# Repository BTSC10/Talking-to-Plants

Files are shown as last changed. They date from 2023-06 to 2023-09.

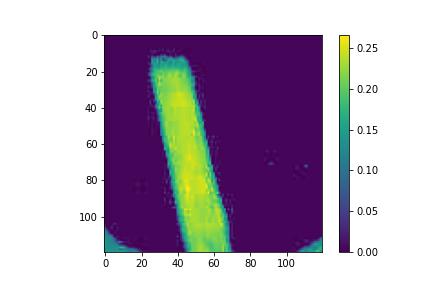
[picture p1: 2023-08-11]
Code/Offline Processing/Cultivar_assessment_SMFI/SMFI_stack__node_2_period_10_20230811_1433/false_coloured_stack/false_colour_91.jpg

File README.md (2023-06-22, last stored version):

# Talking-to-Plants
“Talking to Plants” via Active Digital Image Processing: Industry 4.0, IoT, Technology for Future Farming

This project is built upon the work complete by the below team members, where the project was continued as a Summer Internship

## Team Members:
| name  | user |
| ------------- | ------------- |
| Justin Tan | JSTUN9 |
| David Mohammadi | davidmo13|
| Momin Anwar | mominanwar|
| Mujhtaba Afzal | Gunflower123 |
| Sam Ryder | SamRyder |
| Flavia Dumitrica | flaviamihaela |
| Marton Gonczy | martongonczy |
| Artur Cruz | ArturCr |

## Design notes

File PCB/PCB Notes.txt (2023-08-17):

U14 - GND, SMFI LEDs not working ( + one set wrong way round, and one not working),

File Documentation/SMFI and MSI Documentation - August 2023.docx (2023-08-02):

SMFI AND MSI DOCUMENTATION

August 2023

Contents

# 1 Introduction

This document serves as the main documentation for the system develop during the 2022-23 academic year as the “Talking to plants” team project and the continuation of this work over the summer of 2023 – by Samuel Ryder and David Mohammadi. The system has been split up by subsystem – e.g., image capture, and gateway –, where both hardware and software are documented.

Currently two modes of operation exist for the device – MSI and SMFI. In SMFI mode one group of LEDs is sinusoidally modulated and a set number of images captured during one period. During MSI a single image is taken for each set of LEDs – 16 channels currently implemented.

# 2 Image Capture

## 2.1 Camera board

For this system the OpenMV H7 [1] is utilised, a global shutter module is also installed on this [2]. Further modifications are made to the camera: the included filter has been removed and replaced with an external filter [3].

## 2.2 LED board

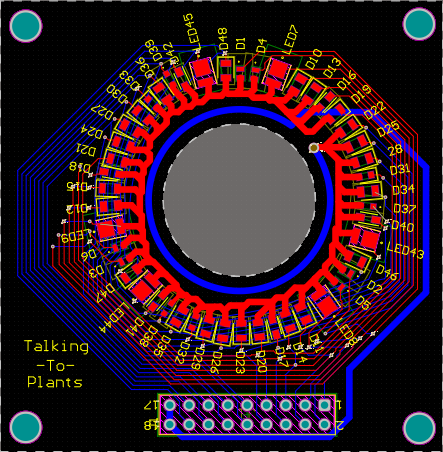
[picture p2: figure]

Figure 1, LED Board

Figure 2, LED Channel connections

Figure 1 shows the current configuration of the LED board, here 16 channels of 3 LEDs (48 in total) are connected. The LEDs within each channel are connected as shown in Figure 2. The wavelengths and chosen LEDs for each channel are listed in Table 1 below,

Table 1, LED Channels

Channel No. | Wavelength | LED
0
1
2 (SMFI)
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
The LED board PCB and schematic are given in [4].

## 2.3 LED Driver

The LED Driver serves to take the signals output from the camera and drive the LEDs, as well as this it serves as a connection between the camera and base box. The PCBs for this are given in [5].

The operation of driving the LEDs is explained below,

- The camera selects the appropriate output from the 1-to-16 multiplexer, where each output corresponds to one channel
- The camera output is set to a predetermined level
- A current driver is powered by this
- Current is sank through this via a header connecting to the LEDs

All channels – bar Channel 2 – show the same configuration, an LED driver connected to an output of the 1-to-16 multiplexer and the LED board header. Channel 2 is configured differently as this channel has the option of either being used in MSI or SMFI mode. Here after the 1-to-16 multiplexer output another multiplexer is found, this is a 1-to-2 multiplexer that allows either for an LED driver to be used (MSI), or a transistor (SMFI).

## 2.4 Camera Code

Two versions of camera code are provided in [6], SMFI and SMFI_MSI. Both operate in the same functionality, however, SMFI is used with the old hardware and SMFI_MSI with the new. Also, as can be seen from the names one is just SMFI and the other both modes. For sake of compactness only SMFI_MSI will be detailed here.

The basic operation of the code can be thought of as below,

- Setup is performed
- When an image capture is triggered, whether by button or timer, execute the main loop of code
- Set the multiplexers selects to match the desired operation
- Output the LED values
- Capture images
- Transmit images
- Perform more captures if required, or, update run parameters from cloud

The individual sections of code are described more thoroughly below.

# 3 References

[1] - https://openmv.io/products/openmv-cam-h7

[2] - https://openmv.io/products/global-shutter-camera-module

[3] - https://www.chroma.com/products/parts/at690-50m

[4] - https://github.com/SamRyder/Talking-to-Plants-Summer-Work/tree/main/PCB/LED%20Board

[5] - https://github.com/SamRyder/Talking-to-Plants-Summer-Work/tree/main/PCB/LED%20Driver

[6] - https://github.com/SamRyder/Talking-to-Plants-Summer-Work/tree/main/Code/Open%20MV%20Camera/Production_CODE

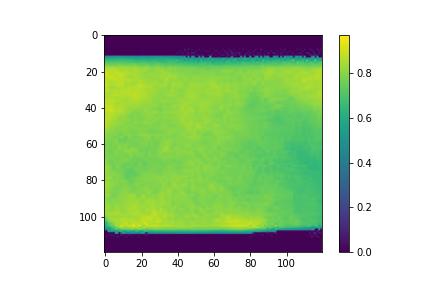
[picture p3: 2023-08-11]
Code/Offline Processing/Cultivar_assessment_SMFI/SMFI_stack__node_2_period_10_20230811_1407/false_coloured_stack/false_colour_89.jpg

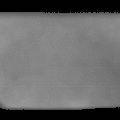
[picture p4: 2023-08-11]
Code/Offline Processing/Cultivar_assessment_SMFI/SMFI_stack__node_2_period_10_20230811_1407/Leaf-10s_fluorescence-frameno28.jpg

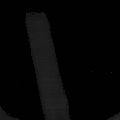
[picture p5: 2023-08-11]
Code/Offline Processing/Cultivar_assessment_SMFI/SMFI_stack__node_2_period_10_20230811_1433/Leaf-10s_fluorescence-frameno17.jpg

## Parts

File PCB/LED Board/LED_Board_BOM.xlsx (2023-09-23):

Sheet: LED_64_V1.3_BOM
Channel | Waveband | Part # | Qty/PCB | Qty | Mouser # | Mouser Link
0 | 395nm | ATS2012UV395 | 4 | 20 | 604-ATS2012UV395 | https://www.mouser.co.uk/ProductDetail/Kingbright/ATS2012UV395?qs=%252BEew9%252B0nqrCgwxEBSEvg7Q%3D%3D
1 | 415nm | ATS2012UV415 | 4 | 20 | 604-ATS2012UV415 | https://www.mouser.co.uk/ProductDetail/Kingbright/ATS2012UV415?qs=%252BEew9%252B0nqrDGuxxVD3buAQ%3D%3D
2 | 450nm | 150283DS73103 | 4 | 20 | 710-150283DS73103 | https://www.mouser.co.uk/ProductDetail/Wurth-Elektronik/150283DS73103?qs=GedFDFLaBXFC8uVfOF%252Bhgw%3D%3D
3 | 470nm | 599-0191-007F | 4 | 20 | 645-599-0191-007F | https://www.mouser.co.uk/ProductDetail/Dialight/599-0191-007F?qs=gTYE2QTfZfTbWzs5Ohdbbg%3D%3D
4 | 528nm | IN-S85ATG | 4 | 20 | 743-IN-S85ATG | https://www.mouser.co.uk/ProductDetail/Inolux/IN-S85ATG?qs=fAHHVMwC%252BbhWv0EIR%2FKEPw%3D%3D
5 | 850 nm | SML-H15RTT86 | 4 | 20 | 755-SML-H15RTT86 | https://www.mouser.co.uk/ProductDetail/ROHM-Semiconductor/SML-H15RTT86?qs=1Kr7Jg1SGW%2FQ1sW3SWCacg%3D%3D
6 | 555 nm | APT2012PGW | 4 | 20 | 604-APT2012PGW | https://www.mouser.co.uk/ProductDetail/Kingbright/APT2012PGW?qs=SxaZfIVsCL2edu2fuRiRPw%3D%3D
7 | 570nm | 150080VS75000 | 4 | 20 | 710-150080VS75000 | https://www.mouser.co.uk/ProductDetail/Wurth-Elektronik/150080VS75000?qs=LlUlMxKIyB0tGHJmO6%252B0ug%3D%3D
8 | 585nm | CMD17-21VYC/TR8 | 4 | 20 | 606-CMD17-21VYC | https://www.mouser.co.uk/ProductDetail/VCC/CMD17-21VYC-TR8?qs=QPnOXzBHpPCjf5SXvJ9GXg%3D%3D
9 | 590nm | 150080YS75000 | 4 | 20 | 710-150080YS75000 | https://www.mouser.co.uk/ProductDetail/Wurth-Elektronik/150080YS75000?qs=LlUlMxKIyB3k0fZGrDMI2w%3D%3D
10 | 610nm | APT1608SECK-AMT | 4 | 20 | 604-APT1608SECK-AMT | https://www.mouser.co.uk/ProductDetail/Kingbright/APT1608SECK-AMT?qs=HAsGzNL9tMp3mOCQHd8jLg%3D%3D
11 | 625nm | APT2012LSECK/J3-PRV | 4 | 20 | 604-APT2012LSECKJ3RV | https://www.mouser.co.uk/ProductDetail/Kingbright/APT2012LSECK-J3-PRV?qs=6oMev5NRZMEkGJkKIsAalQ%3D%3D
12 | 640nm | APT1608SEC/J3-AMT | 4 | 20 | 604-APT1608SEC/J3AMT | https://www.mouser.co.uk/ProductDetail/Kingbright/APT1608SEC-J3-AMT?qs=0pUdBCiL%2F4PrQrm2zkbL8w%3D%3D
13 | 660nm | SML-LXF0805SRD-TR | 4 | 20 | 696-LXF0805SRD-TR | https://www.mouser.co.uk/ProductDetail/Lumex/SML-LXF0805SRD-TR?qs=26yrLECgo488zNHkE34vSA%3D%3D
14 | 730nm | 150283FS73103 | 4 | 20 | 710-150283FS73103 | https://www.mouser.co.uk/ProductDetail/Wurth-Elektronik/150283FS73103?qs=GedFDFLaBXFYj4r0ZVjyhg%3D%3D
15 | 880nm | APT2012SF4C-PRV | 4 | 20 | 604-APT2012SF4C-PRV | https://www.mouser.co.uk/ProductDetail/Kingbright/APT2012SF4C-PRV?qs=f499HRGa1RnfiWuPE%2FmgSQ%3D%3D
- | - | 61301821121 | 1 | 5 | 710-61301821121 | https://www.mouser.co.uk/ProductDetail/Wurth-Elektronik/61301821121?qs=PhR8RmCirEaqwz8GJH1NvA%3D%3D
 |  | Total Units | 5

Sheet: LED_48_BOM
Channel | BOM Part number | Waveband | Requested Part Number | Requested Waveband | Action
0 | ATS2012UV395 | 395nm | 604-ATS2012UV395 | 395nm
1 | ATS2012UV395 | 395nm | 604-ATS2012UV415 | 415nm | Replace with ATS2012UV415 as requested (same footprint)
2 | 150283DS73103 | 450nm | Wurth Elektronik 150283DS73103 | 450nm
3 | 599-0191-007F | 470nm | 645-599-0191-007F | 470nm
4 | IN-S85ATG | 528nm | 743-IN-S85ATG | 528nm
5 | LT_M673-P2R1-25-Z | 532nm | SML-H15RTT86 (850 nm) | 700 to 880 | find LED between 700 and 880 DONE
6 | SML-LX0805UWC-TR | White | APT2012PGW (555 nm) | 550nm | Find 550nm Replacement DONE
7 | 150080VS75000 | 570nm | 710-150080VS75000 | 570nm
8 | CMD17-21VYC/TR8 | 585nm | 606-CMD17-21VYC | 585nm
9 | 150080YS75000 | 590nm | 710-150080YS75000 | 590nm
10 | APT1608SECK-AMT | 610nm | 696-SML-F0805SOCTR | 610nm | Wavelengths match, ignore Requested LED
11 | APT2012LSECK/J3-PRV | 640nm | 604-APT2012LSECKJ3RV | 625nm
12 | APT1608SEC/J3-AMT | 640nm | 604-APT2012SRCPRV | 640nm | Wavelengths match, ignore Requested LED
13 | LT_M673-P2R1-25-Z | 532nm | 696-LXF0805SRD-TR | 660nm | Replace with requested part, change PCB footprint, DONE
14 | 150283FS73103 | 730nm | 696-SML-15HC-RPTR | 700nm | Wavebands similar, ignore Requested LED
15 | APT2012SF4C-PRV | 880nm | 604-APT2012SF4C-PRV | 880nm
 | 61301821121

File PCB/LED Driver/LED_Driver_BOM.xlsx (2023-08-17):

Comment | Designator | Footprint | LibRef | Quantity
OpenMV H7 Headers | C | OPENMV H7 | OpenMV H7 Headers | 1
1206YC105KAT2A | C1 | FP-1206-L_3_2_0_2-W_1_6_0-IPC_A | CMP-04427-000085-1 | 1
SSQ-102-01-G-S | J1 | SMTC-SSQ-102-01-X-S | CMP-1023-00275-1 | 1
90120-0763 | J2 | FP-90120-0763-MFG | CMP-04776-000084-1 | 1
61301821121 | J3 | 61301821121 | CMP-1502-01101-2 | 1
MTC-8810SB | J3 | MTC8810SB | MTC-8810SB | 1
SPP20N60C3 | Q1 | INF-PG-TO220-3-1 | CMP-1164-00011-1 | 1
15R 5% 1206(3216) | R0, R1, R2, R3, R4, R5, R6, R7, R8, R9, R10, R11, R12, R13, R14, R15 | RESC1206(3216)_M | CMP-1014-00030-1 | 16
RC1206FR-07100RL | R16 | RESC3116X65X40ML10T20 | CMP-2100-03675-1 | 1
18R 1% 1206(3216) | R17, R18, R19, R20, R21, R22, R23, R24, R25, R26, R27, R28, R29, R30, R31, R32, R33 | RESC1206(3216)_M | CMP-1014-00311-1 | 17
CD74HC4067M96 | U1 | FP-DW0024A-MFG | CMP-04901-000007-1 | 1
BCR420U | U2, U3, U4, U5, U6, U7, U8, U9, U10, U11, U12, U13, U14, U15, U16, U17 | INF-SC74_N | CMP-1139-00012-1 | 16
Multiplexer Switch IC | U18 | FP-DBV0006A-IPC_A | CMP-0859-00203-4 | 1
OpenMV_M7 (Shield) | U19 | OPENMV_M7(32.48MM) |  | 1

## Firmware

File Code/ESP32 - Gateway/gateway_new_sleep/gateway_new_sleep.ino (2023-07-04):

#include "driver/gpio.h"
#include "painlessMesh.h"
#include <ArduinoJson.h>
#include <Arduino.h>
#include <HardwareSerial.h>
#include <string.h>
#include <WiFi.h>
#include <HTTPClient.h>
#include <WiFiClient.h>
#include <stdio.h>
#include <stdbool.h>

HardwareSerial SerialPort(2); // use UART2

#define size 7000

//const char* ssid = "Justin";
//const char* password = "justintan";

const char* ssid = "Sam’s IPhone";
const char* password = "a1b2c3esp32";

HTTPClient http;

String host = "https://talkingtoplants.online";
String file = "/insertData2.php";
String URL = host + file;
String file2 = "/GetRequest2.php?api_key=CvcCKjGnBYAQoEAWtNGb6BFAdsWATKZwdNip8LVunjdsbQro1VDpVHnwXZAs8Sog";
String URL2 = host + file2;
String ApiKey = "CvcCKjGnBYAQoEAWtNGb6BFAdsWATKZwdNip8LVunjdsbQro1VDpVHnwXZAs8Sog";


// Defines the LED pin locations
const int led_r=22; // Red LED
const int led_y=23; // Yellow LED
const int led_g=14; // Green LED
const int empty=32; // Avaliable for an LED / Button / Switch

void Blink(int pin, int ms){
  digitalWrite(pin, HIGH); // turn the LED on (HIGH is the voltage level)
  //delay(ms);               // wait for a second
  //digitalWrite(pin, LOW);  // turn the LED off (LOW is the voltage level)
}
void Off (int pin){
  digitalWrite(pin, LOW); 
}


bool flag = false; 
bool flag2 = true;
bool flag3 = false;
bool start = false;
uint8_t imageNum = 0;
uint8_t segmentNum = 0;
uint8_t totalSegmentNum = 0;
uint8_t runNum = 0;
uint8_t period = 0;
uint8_t mode = 0; // SMFI = 0, MSI = 1

unsigned long number = 0;
uint8_t buff[7000];
char msg[size];
int bufferPoint = 0;
int nodeID = 123;
int period1 ;
int period2 ;
int period3 ;
int mode_new ; // SMFI = 0, MSI = 1
uint8_t numImage = 2;
uint8_t freqCount = 0;
int timeDiff ;
uint8_t headerSize = 9;
// tables arrays for lookup fast
static bool __TABLE_INIT= false;
static unsigned int TABLE_EV[256];


unsigned char reverse(unsigned char b) {
   b = (b & 0xF0) >> 4 | (b & 0x0F) << 4;
   b = (b & 0xCC) >> 2 | (b & 0x33) << 2;
   b = (b & 0xAA) >> 1 | (b & 0x55) << 1;
   return b;
}

// input is start of char array address & n == number of bytes
unsigned int CRC32_Table(unsigned char  * bytes, int n)
{
    const unsigned int polynomial = 0x04C11DB7; /* divisor is 32bit */
    unsigned int crc = 0xffffffff; /* CRC value is 32bit */
    unsigned char b;
    unsigned char bk;

    if (__TABLE_INIT) {
        // nothing to do - follow by lookup
    } 
    else {
        // init all tables first 
            for (int j = 0; j < 256; j++){
             b = j; crc = 0;
                     crc ^= (unsigned int)(b << 24);  //move byte into MSB of 32bit CRC 
                     for (int k = 0; k < 8; k++)
                     {
                         if ((crc & 0x80000000) != 0)  //test for MSB = bit 31 
                         {
                             crc = (unsigned int)((crc << 1) ^ polynomial);
                         }
                         else
                         {
                             crc <<= 1;
                         }
                     }
             // now add value to table
             TABLE_EV[j] = crc;
        } // j 0-255
            __TABLE_INIT = true;
    }
    // start calculations
    crc = 0xffffffff; /* CRC value is 32bit */

    for (int j=0; j<n; j++)
    {
        b = bytes[j];
        b = reverse(b); bk = b;
        b = b ^ ((crc>>24) & 0x0ff);
        crc = (crc<<8) ^ TABLE_EV[b]; 
        //printf("2..Computing for %x %x is %x\n",bk,b,crc);

    }

    crc = crc ^ 0xffffffff;
    // NOW REVERSE COMPLETE 32 bit WORD BIT BY BIT 
    crc = 
        reverse((crc & 0xff000000)>>24)   + 
    (reverse((crc & 0x00ff0000)>>16)<<8)   + 
    (reverse((crc & 0x0000ff00)>>8)<<16)   + 
    (reverse((crc & 0x000000ff))<<24) ;

    return crc;
}

void sendMessage(){
  // can be used to add functionality
  // generate msg
  flag = true;
  Serial.println(bufferPoint);
  // read buffer to update ID number & segment number
  // 1st 4 bytes == nodeID
  // 5th = imageNum
  // 6th = segment Num
  // 7th = totalSegNum
  // 8th = Period
  // 9th = runNum
  // 10th = mode
  char byte1 = buff[0];
  char byte2 = buff[1];
  char byte3 = buff[2];
  char byte4 = buff[3];
  number = (static_cast<unsigned long>(byte1) << 24) |
                           (static_cast<unsigned long>(byte2) << 16) |
                           (static_cast<unsigned long>(byte3) << 8) |
                           static_cast<unsigned long>(byte4);
  imageNum = buff[4];
  segmentNum = buff[5];
  totalSegmentNum = buff[6];
  period = buff[7];
  runNum = buff[8];
  mode = buff[9];

  //strncpy(msg, buff, bufferPoint); // copy first ith elements from buff into msg
  // set msg to be null terminator
  //buff[bufferPoint] = '\0';
  msg[0] = 0;
  // start from 4th index => 1&2 are image number , 3&4 are segment number
  //sprintf(msg+strlen(msg),"0x");
  for (int i = headerSize; i < bufferPoint; i++){
    sprintf(msg + strlen(msg), "%02.2X", buff[i]);
  }
  bufferPoint = 0;
  Off(led_r);
  Off(led_y);
  Off(led_g);
  // change LED depending on period
  if ((period & (1 << 0)) != 0){
    // blink red
    Blink(led_r,10);
  }
  if ((period & (1 << 1)) != 0){
    // blink Yellow
    Blink(led_y,10);
  }
  if ((period & (1 << 2)) != 0){
    // blink Green
    Blink(led_g,10);
  }
};

void setup() {
  Serial.begin(115200);
  SerialPort.begin(115200, SERIAL_8E1, 16, 17); 
  // 16 is RX
  // 17 is TX
  WiFi.begin(ssid, password);
  Serial.println("Connecting");
  while(WiFi.status() != WL_CONNECTED) {
    delay(1000); // delay 1 sec
    Serial.print(WiFi.status());
    Serial.println(" ...");
  }
  Serial.print("Connected with IP: ");
  Serial.println(WiFi.localIP());
  Serial.println("");
  pinMode(led_r, OUTPUT); //Configure the Red LED ...
  pinMode(led_y, OUTPUT);
  pinMode(led_g, OUTPUT);
}

void loop() {
  //Check WiFi connection case 2 
  if (flag){
    if(WiFi.status()== WL_CONNECTED){
      // Start Connection to Server

      bool httpBegin = http.begin(URL);

      int httpResponseCode = 0;
      String httpPayloadResponse = "";

      // Check HTTP connection
      if (httpBegin) {
        Serial.println("HTTP Connected");
        // while HTTP Response is wrong => we repeat 3 times
        int httpCounter = 0;
        while (httpResponseCode != 200 ){
          if ( httpCounter >= 3){
            break;
          }
          //String ImageData = String(UARTRecieved);
          String ImageData = String(msg);
          Serial.println("this is packet data");
          Serial.println(number);
          Serial.println(runNum);
          Serial.println(imageNum);
          Serial.println(segmentNum);
          Serial.println(totalSegmentNum);
          Serial.println(period);
          Serial.println(ImageData);
          Serial.println(mode);

          String payload = "api_key=" + ApiKey + "&NodeID=" + String(number) + "&RunNumber=" + String(runNum) + "&ImageNumber=" + String(imageNum) + "&SegmentNumber=" + String(segmentNum) + "&TotalSegmentNumber="+ String(totalSegmentNum)+"&Period="+String(period)+ "&Data=" + String(ImageData)+ "&Mode=" + String(mode);
          http.addHeader("Content-Type", "application/x-www-form-urlencoded");

          // Send message, get response code and message
          httpResponseCode = http.sendRequest("POST", payload);
          httpPayloadResponse = http.getString();
          httpCounter +=1;
        }
        // End connection
        http.end();
      }
      else {
        Serial.println("HTTP Connection Unsuccessful");
      }
      // Print response code and message
      Serial.println("");
      Serial.println("Data Sent, Response Code: ");
      Serial.println(httpResponseCode);
      Serial.println("Payload Response: ");
      Serial.println(httpPayloadResponse);


      Serial.println("Check values");
      if (imageNum == numImage){
        // one frequency run is done
        freqCount +=1;
      }
      if (imageNum == numImage && segmentNum == totalSegmentNum && freqCount == 3){
        Serial.println("Getting new Freq values");
        flag3 = true;

        // update Period through GET request
        // new server name => 
        bool httpBegin2 = http.begin(URL2);

        int httpResponseCode2 = 0;
        String httpPayloadResponse2 = "";
        // Check HTTP connection
        if (httpBegin2) {
          Serial.println("HTTP GET Connected");
          // while HTTP Response is wrong => we repeat 3 times
          int httpCounter2 = 0;
          while (httpResponseCode2 != 200 ){
            if ( httpCounter2 >= 3){
              break;
            }

            httpResponseCode2 = http.sendRequest("GET");
            httpPayloadResponse2 = http.getString();
            Serial.println(httpPayloadResponse2);
            httpCounter2+=1;
          }
          DynamicJsonDocument doc(1000);
          // Deserialize the JSON string
          DeserializationError error = deserializeJson(doc, httpPayloadResponse2);
          if (error) {
            Serial.print("JSON parsing failed: ");
            Serial.println(error.c_str());
            return;
          }
          // Access each individual periods
          period1 = doc["Frequency1"].as<int>();
          period2 = doc["Frequency2"].as<int>();
          period3 = doc["Frequency3"].as<int>();
          numImage = doc["NumImage"].as<uint8_t>();
          timeDiff = doc["timeDiff"].as<int>();
          mode_new = doc["timeDiff"].as<int>();
          
          // Print the frequencies
          Serial.print("Period 1: ");
          Serial.println(period1);
          Serial.print("Period 2: ");
          Serial.println(period2);
          Serial.print("Period 3: ");
          Serial.println(period3);
          Serial.print("Run Image Num: ");
          Serial.println(numImage);
          Serial.print("Sleep Time: ");
          Serial.println(timeDiff);
          Serial.print("Mode: ");
          Serial.println(mode_new);

          // End connection
          http.end();
        }
        else {
          Serial.println("HTTP Connection Unsuccessful");
        }
        // Print response code and message
        Serial.println("");
        Serial.println("Period Received, Response Code: ");
        Serial.println(httpResponseCode2);
        Serial.println("Payload Response: ");
        Serial.println(httpPayloadResponse2 );
      }
    }
    else {
      Serial.println("WiFi Not Connected");
    }
    
    flag = false;
    start = false;
    // send back signal to uart => to start next cycle
    
    if(flag3){
      flag3 = false;
      Serial.println("Sending Period Values");
      SerialPort.write("\n");
      SerialPort.write(period1);
      SerialPort.write(period2);
      SerialPort.write(period3);
      SerialPort.write(numImage);
      SerialPort.write(mode_new);
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

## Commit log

2023-06-22 Upload of PCB design
    [Initial Design.kicad_pcb, Initial Design.sch]
2023-06-22 File restructure
    [Initial Design.kicad_pcb, Initial Design.sch]
2023-06-26 Addition to Processing
    [reference.csv]
2023-07-10 Correct Run
    [difference_data.csv]
2023-08-02 I think it works now
    [difference_data.csv, fluorescence_response_data.csv]
2023-09-02 Redesign PCB physical layout
    Change LED circular layout to rectangular layout, change board dimensions
    [LED_48.PcbDoc, LED_48.SchDoc]
2023-09-23 Add BOM for LED Board V1.3
    [LED_Board_BOM.xlsx]
2023-09-23 Add LED Board V1.3 PCB file
    Add Altium .PcbDoc file for V1.3 of the LED Board PCB design
    [LED_64_V1.3.PcbDoc]
